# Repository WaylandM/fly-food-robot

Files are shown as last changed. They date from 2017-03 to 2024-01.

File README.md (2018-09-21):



# Cartesian coordinate robot for dispensing fruit fly food

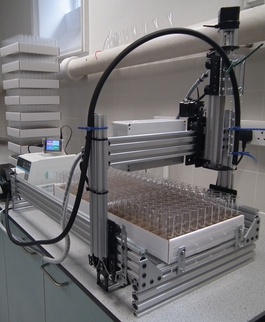
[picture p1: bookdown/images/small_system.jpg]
CNC fly food dispenser


Video: https://doi.org/10.6084/m9.figshare.5175223.v1

## Hardware documentation
The build of the hardware is described on [docubricks](http://docubricks.com/):
[CNC fly food dispenser](http://docubricks.com/viewer.jsp?id=8652757760093769728)

Source of the docubricks documentation:
https://github.com/WaylandM/fly-food-robot/tree/master/docubricks

## Software 
Source code:
https://github.com/WaylandM/fly-food-robot/tree/master/raspberrypi/robot/

## Operating instructions
A bookdown book describing software installation, configuration and operation of the robot can be found here:
https://waylandm.github.io/fly-food-robot/

## Publication
An article providing an overview of this project has been published in the [Journal of Open Hardware](https://openhardware.metajnl.com/):
https://openhardware.metajnl.com/articles/10.5334/joh.9/

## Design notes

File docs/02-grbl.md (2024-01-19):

# Grbl installation and configuration {#grbl}

## Overview

CNC motion control is provided by grbl (https://github.com/gnea/grbl), an open source, embedded, high performance g-code parser. Grbl is written in optimized C and runs directly on an Arduino. This is used in conjunction with the gShield (formerly known as grblshield) which provides the hardware drivers for the stepper motors. Grbl sends out TTL signals on pins A3 and 13 of the Arduino to control coolant flow and spindle direction, respectively. Here these signals are used to remotely control a peristaltic pump. 

## Flashing Grbl to Arduino

To flash Grbl to the Arduino you will need a computer with the latest version of the [Arduino IDE](https://www.arduino.cc/en/Main/Software) installed. The following instructions for flashing Grbl to the Arduino are taken from: https://github.com/gnea/grbl/wiki/Compiling-Grbl

_**NOTE: Before starting, delete prior Grbl library installations from the Arduino IDE. Otherwise, you'll have compiling issues! On a Mac, Arduino libraries are located in ```~/Documents/Arduino/libraries/```. On Windows, it's in ```My Documents\Arduino\libraries```.**_

1. Download the Grbl source code.
 * Open the following page in your web browser: https://github.com/gnea/grbl
 * Click on the ```<>Code``` Tab
 * Click the ```Clone or Download``` green button on the Grbl home page.
 * Click the ```Download ZIP```
 * Unzip the download and you'll have a folder called ```grbl-XXX```, where `XXX` is the release version. 

2. Launch the Arduino IDE (figure \@ref(fig:arduinoIDE))
 * Make sure you are using the most recent version of the Arduino IDE!

<div class="figure" style="text-align: center">
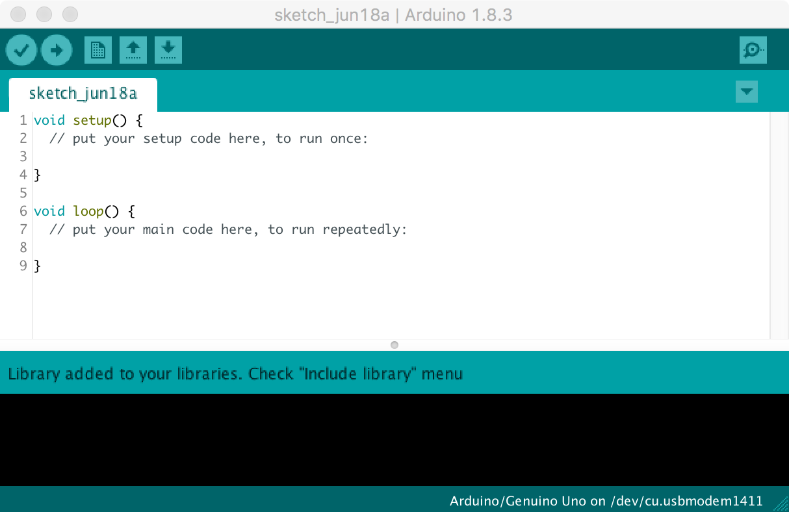
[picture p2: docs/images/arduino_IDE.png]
Arduino IDE

<p class="caption">(\#fig:arduinoIDE)Arduino IDE</p>
</div>

3. Load Grbl into the Arduino IDE as a Library.
 * Click the ```Sketch``` drop-down menu, navigate to ```Include Library``` and select ```Add .ZIP Library```.
 * **IMPORTANT:** Select the ```Grbl``` folder **_inside_** the ```grbl-XXX``` folder, which **only** contains the source files and an example directory (figure \@ref(fig:addGrblLib)).
 
<div class="figure" style="text-align: center">
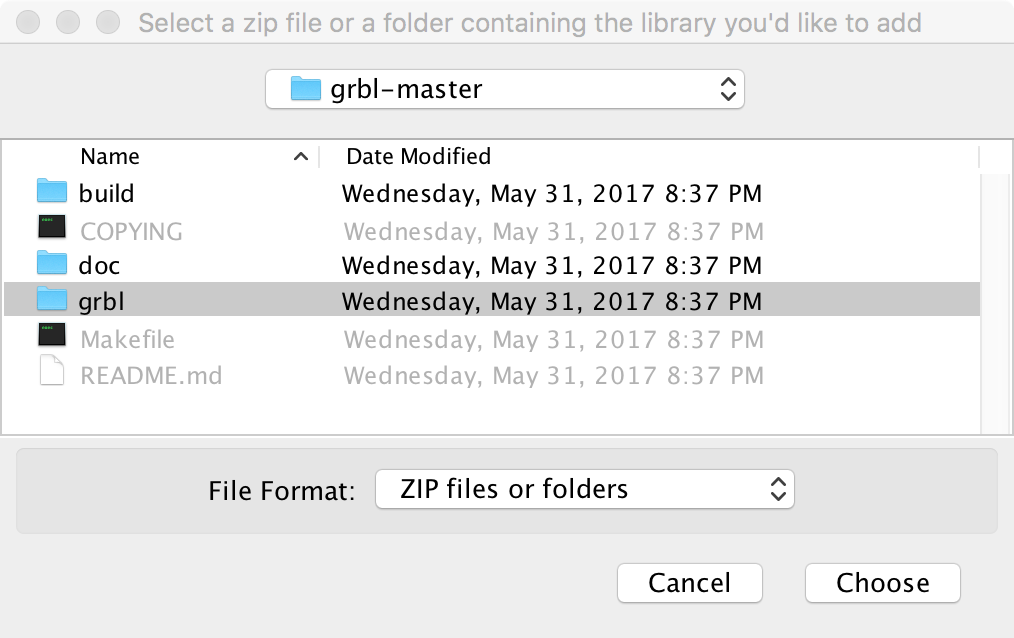
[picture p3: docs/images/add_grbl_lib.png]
Loading Grbl library into the Arduino IDE

<p class="caption">(\#fig:addGrblLib)Loading Grbl library into the Arduino IDE</p>
</div>

 * If you accidentally select the `.zip` file or the wrong folder, you will need to navigate to your Arduino library, delete the mistake, and re-do Step 3.
 
4. Open the `GrblUpload` Arduino example.
 * Click the ```File``` drop-down menu, navigate to ```Examples->Grbl```, and select ```GrblUpload``` (figure \@ref(fig:grblUploadFile)).

<div class="figure" style="text-align: center">
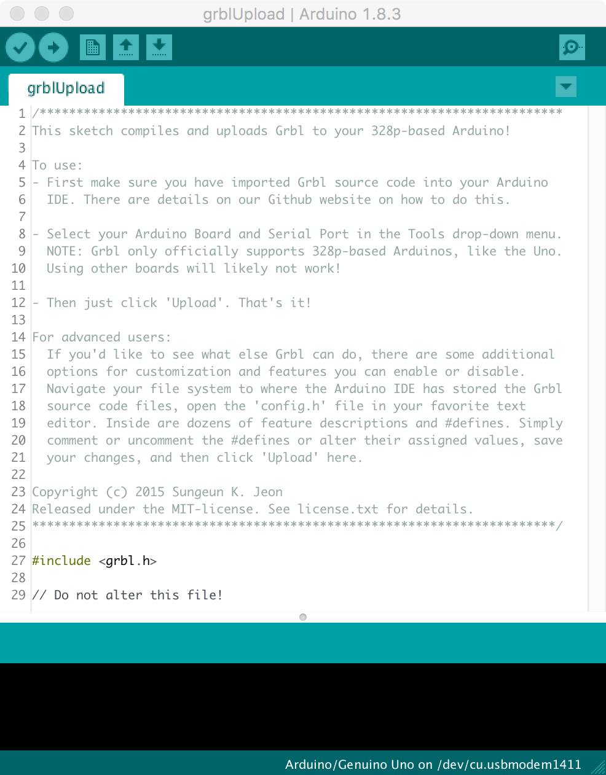
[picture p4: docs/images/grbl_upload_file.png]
GrblUpload example file

<p class="caption">(\#fig:grblUploadFile)GrblUpload example file</p>
</div>

5. Compile and upload Grbl to your Arduino.
 * Connect your computer directly to the Arduino using the USB cable. Unplug the USB cable from the raspberry pi and plug it into your computer. Remember to reconnect the raspberry pi to the Arduino after you have finished configuring Grbl (figure \@ref(fig:laptop2arduino)).

<div class="figure" style="text-align: center">
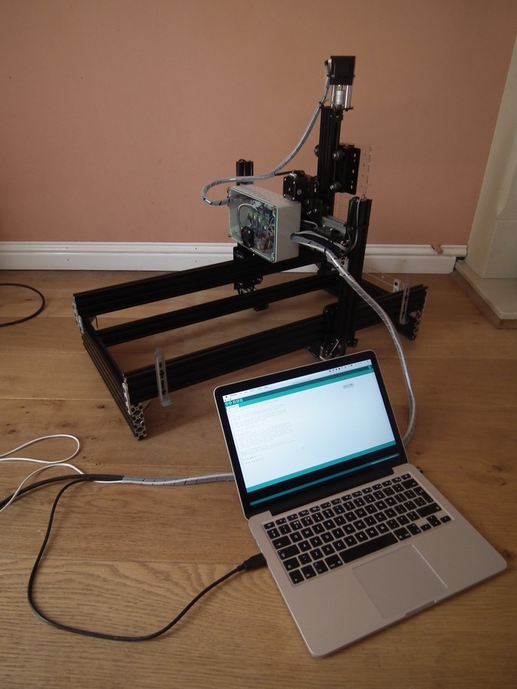
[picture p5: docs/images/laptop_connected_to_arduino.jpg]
Laptop connected directly to Arduino

<p class="caption">(\#fig:laptop2arduino)Laptop connected directly to Arduino</p>
</div>

 * Make sure your board is set to the Arduino Uno in the ```Tool->Board``` menu and the serial port is selected correctly in ```Tool->Serial Port```. 
 * Click the ```Upload```, and Grbl should compile and flash to your Arduino! (Flashing with a programmer also works by using the ```Upload Using Programmer``` menu command.)

## Check serial connection to Grbl

_**NOTE: Before powering up the gShield and motors, check that the actuator carriages for all three axes are approximately centred (figure \@ref(fig:actuatorsCentred)). Initially we do not know in which direction the actuator carriages will travel when G-code commands are issued, so positioning each in the middle of its range reduces the risk of collisions with the end stops.**_

<div class="figure" style="text-align: center">
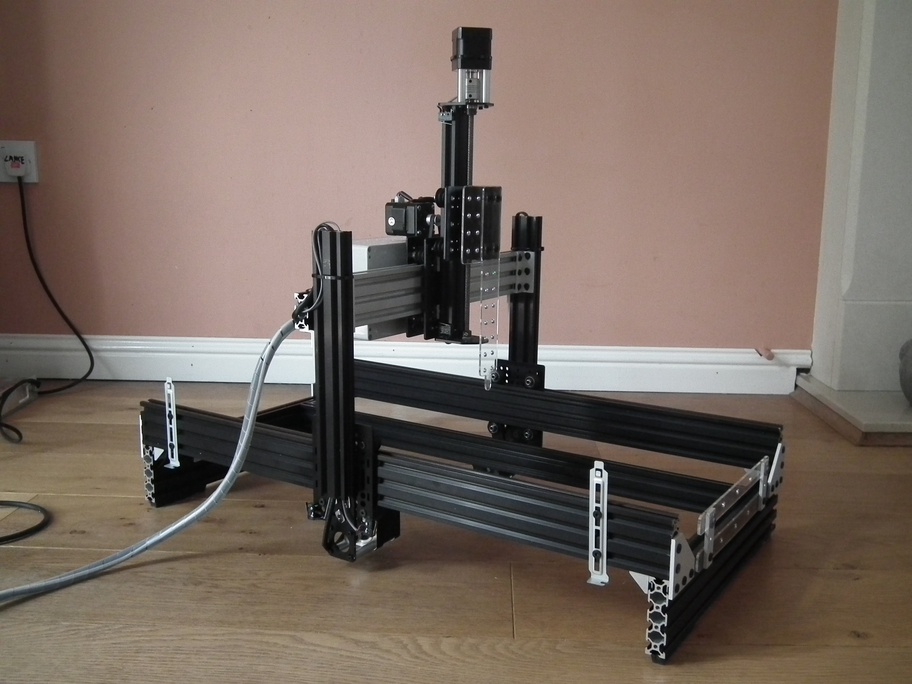
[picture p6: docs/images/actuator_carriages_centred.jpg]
Actuator carriages centred in preparation for powering-up motors for first time

<p class="caption">(\#fig:actuatorsCentred)Actuator carriages centred in preparation for powering-up motors for first time</p>
</div>

1. Open serial monitor in Arduino IDE
 * Click ```Tools``` drop-down menu, and select ```Serial Monitor```

<div class="figure" style="text-align: center">
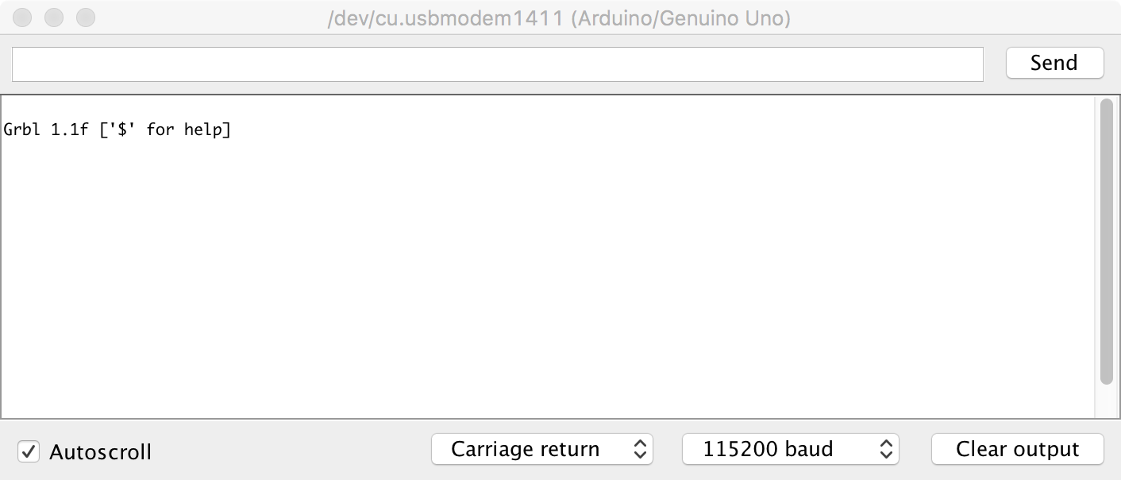
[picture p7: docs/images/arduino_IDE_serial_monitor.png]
Arduino IDE Serial Monitor

<p class="caption">(\#fig:serialMonitor)Arduino IDE Serial Monitor</p>
</div>

 * Note that line-ending is set to ```Carriage return``` and baud rate is set to ```115200``` (figure \@ref(fig:serialMonitor))
2. Try issuing a G-code command. 
 * Type ```?``` and hit return. 
 * This command will report the current position; as we have just started the system up all axes will be at 0.000.
3. Now try moving actuators
 * To move in the x-axis type ```x5``` and hit return. Make a note of the direction in which the actuator carriage moves. N.B. this command tells Grbl to move to the x coordinate that is 5 units from the origin, it is not equivalent to telling the robot to move 5 units in the x-axis.
 * To move in the opposite direction along the x-axis type ```x-5``` and hit return.
 * To return to the starting point, use ```x0```
 * Repeat for the other axes, replacing the x in the commands with y or z. Make a note of the direction the actuator carriages move with each command.

## Grbl configuration

### Read current configuration
 * The ```$$``` command will report Grbl's current configuration.
 * Descriptions of these settings can be found here: https://github.com/gnea/grbl/wiki/Grbl-v1.1-Configuration
 * These settings will be modified in subsequent steps.

### Check directionality of each axis.

<div class="figure" style="text-align: center">
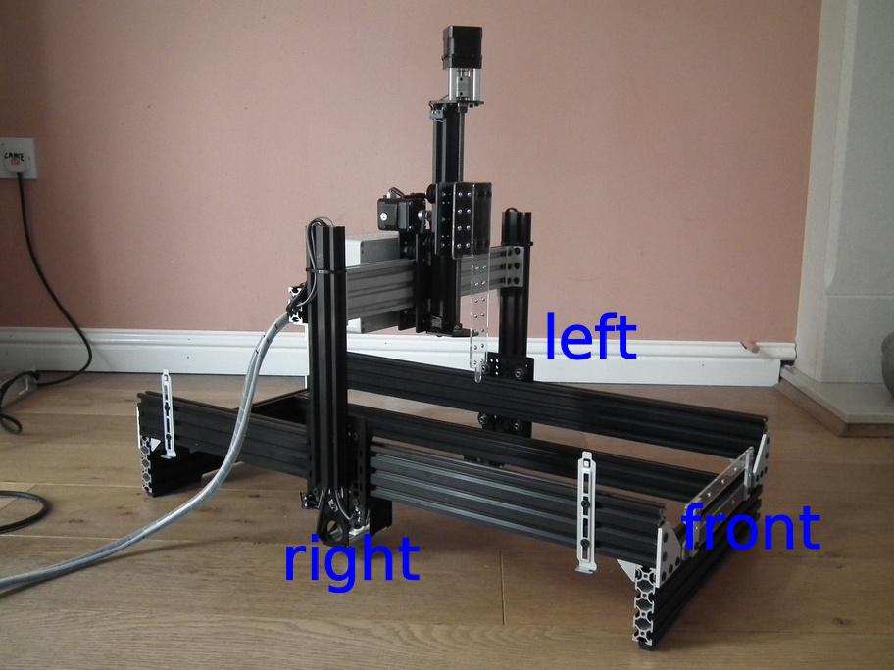
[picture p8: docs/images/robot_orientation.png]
Orientation of robot.

<p class="caption">(\#fig:robotOrientation)Orientation of robot.</p>
</div>

 * Orientation of the robot is shown in figure \@ref(fig:robotOrientation).
 * At present the origins of all three axes are mid-way along each actuator, because this was the position of the actuator carriages when the system was started.
 * Make sure actuator carriages are at their current origin by entering this command: ```x0y0z0```
 * Enter the command: ```x5```. The x-axis carriage should move from right to left (orientation of robot is shown in figure \@ref(fig:robotOrientation). If it doesn't, make a note that it will need to be inverted.
 * Enter the command: ```y5```. The y-axis carriage should move forwards. If it doesn't, make a note that it will need to be inverted.
 * Enter the command: ```z5```. The z-axis carriage should move up. If it doesn't, make a note that it will need to be inverted.
 * The direction of the actuators can be inverted using setting **$3**, the [Direction port invert (mask)](https://github.com/gnea/grbl/wiki/Grbl-v1.1-Configuration#3--direction-port-invert-mask). An appropriate value is selected from table \@ref(tab:invertMaskSettings). For example, to invert the direction of the X and Z axis actuators use the following command: ```$3=5```

<!---
Table: (\#tab:invertMaskSettings) Masks for direction port inversion.

| Setting Value | Mask |Invert X | Invert Y | Invert Z |
|:-------------:|:----:|:-------:|:--------:|:--------:|
| 0 | 00000000 |N | N | N |
| 1 | 00000001 |Y | N | N |
| 2 | 00000010 |N | Y | N |
| 3 | 00000011 |Y | Y | N |
| 4 | 00000100 |N | N | Y |
| 5 | 00000101 |Y | N | Y |
| 6 | 00000110 |N | Y | Y |
| 7 | 00000111 |Y | Y | Y |

 --->

Table: (\#tab:invertMaskSettings)Masks for direction port inversion.

|Setting Value |Mask     |Invert X |Invert Y |Invert Z |
|:-------------|:--------|:--------|:--------|:--------|
|0             |00000000 |N        |N        |N        |
|1             |00000001 |Y        |N        |N        |
|2             |00000010 |N        |Y        |N        |
|3             |00000011 |Y        |Y        |N        |
|4             |00000100 |N        |N        |Y        |
|5             |00000101 |Y        |N        |Y        |
|6             |00000110 |N        |Y        |Y        |
|7             |00000111 |Y        |Y        |Y        |

### Activate hard limits
Hard limits are a safety feature to prevent the machine from travelling beyond the limits of travel. Grbl monitors the paired limit switches on each axis and if a switch is triggered it will immediately switch off all motors. Hard limits are activated by setting **$21** [hard limits ( boolean)](https://github.com/gnea/grbl/wiki/Grbl-v1.1-Configuration#21---hard-limits-boolean) to 1: 
```
$21=1
```

### Setup homing
The homing cycle is used to set the origin of the Cartesian coordinate system used by the robot. During the homing cycle Grbl moves each actuator in the positive direction until the limit switches are triggered. The homing cycle is activated by setting **$22** [homing cycle (boolean)](https://github.com/gnea/grbl/wiki/Grbl-v1.1-Configuration#22---homing-cycle-boolean) to 1: 
```
$22=1
```

Initiate  a homing cycle using the following command: ```$h```. All actuator carriages should move to the origin of their axes. The origin of the Cartesian coordinate system (home) for the robot is shown in figures \@ref(fig:xyOrigin) and \@ref(fig:zOrigin)

<div class="figure" style="text-align: center">
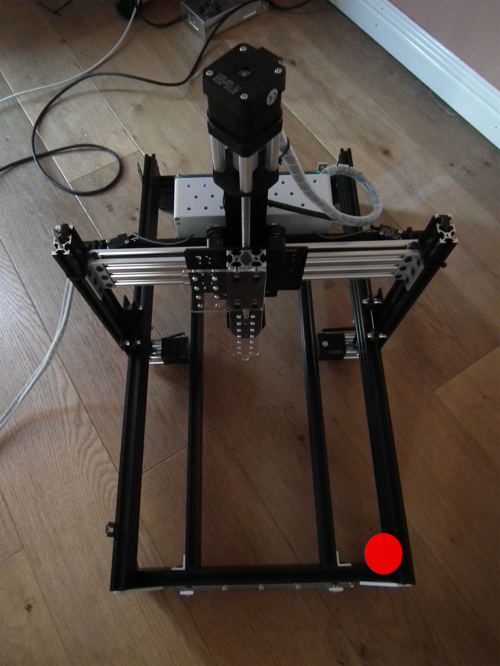
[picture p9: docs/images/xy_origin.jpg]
Origin of XY coordinate system.

<p class="caption">(\#fig:xyOrigin)Origin of XY coordinate system.</p>
</div>

<div class="figure" style="text-align: center">
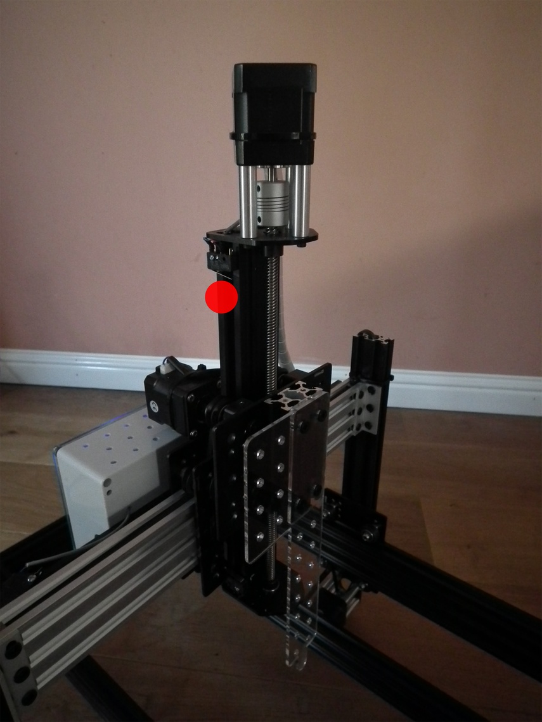
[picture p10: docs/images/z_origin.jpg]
Origin of Z axis.

<p class="caption">(\#fig:zOrigin)Origin of Z axis.</p>
</div>

We also need to set **$24** [homing feed rate](https://github.com/gnea/grbl/wiki/Grbl-v1.1-Configuration#24---homing-feed-mmmin) and **$25** [homing seek rate](https://github.com/gnea/grbl/wiki/Grbl-v1.1-Configuration#25---homing-seek-mmmin). Homing seek rate is the initial speed at which Grbl searches for the limit switches. Once it has them, it makes slower approach at the homing feed rate to get a more precise location for machine zero. We will set homing seek rate to 1000 mm/min ```$24=100``` and homing feed rate to 100 mm/min ```$25=1000```.

At the end of a homing cycle each actuator carriage must be moved off its home limit switch, otherwise the hard limit will be triggered. 
The **$27** [Homing pull-off (mm)](https://github.com/gnea/grbl/wiki/Grbl-v1.1-Configuration#27---homing-pull-off-mm) specifies the distance required to clear the limit switches. For our robot we will use a value of 5mm:
```
$27=5
```

### Motor step size
**$100**, **$101** and **$102** define [[X,Y,Z] steps/mm](https://github.com/gnea/grbl/wiki/Grbl-v1.1-Configuration#100-101-and-102--xyz-stepsmm).
Suitable values for our stepper motors are:
```
$100=40
$101=40
$102=49.673
```

If you are using a different type of stepper motor, the step size can be easily calculated by measuring how far each actuator moves in response to a G-code command. For example, we would calculate the step size for the X actuator as follows.

1. Using the serial monitor in the Arduino IDE, issue the following command to *home* the machine:
```
$h
```

2. Read the current position of the machine, as reported by the Grbl controller:
```
?
```
After homing the Cartesian coordinates should be zero minus the homing pull-off:
* x = -5
* y = -5
* z = -5

3. Make a note of the physical position of the nozzle.

4. Issue a g-code command to move to the -100mm position on the x-axis:
```
x-100
```
Keep decreasing the value of x until the x-actuator carriage almost meets the limit switch on the right hand side of the machine. The greater the distance moved, the more precise our calculation of step-size will be.

5. Query Grbl's machine coordinates:
```
?
```

6. Measure the physical distance travelled along the x-axis in millimetres.

7. Find **$100**, the currently configured step size for the x-axis:
```
$$
```

8. Calculate the correct value for step-size:

```
current_step_size = steps/mm in current configuration
grbl_start = start position reported by Grbl controller (mm)
grbl_end = end position reported by Grbl controller (mm)
physical_distance = physical distance moved by actuator (mm)

steps/mm = -(curr_steps_per_mm * (end_pos_grbl-start_pos_grbl)) / physical_distance
```

### Feed rates and acceleration
**$110**, **$111** and **$112** set the [maximum rates (mm/min)](https://github.com/gnea/grbl/wiki/Grbl-v1.1-Configuration#110-111-and-112--xyz-max-rate-mmmin) for the X, Y and Z actuators, respectively. We will use the following values:
```
$110=5000
$111=5000
$112=2500
```

[Acceleration (mm/sec^2)](https://github.com/gnea/grbl/wiki/Grbl-v1.1-Configuration#120-121-122--xyz-acceleration-mmsec2) is set to 50 for all axes:
```
$120=50
$121=50
$122=50
```

### Summary of settings
```
$0=10
$1=25
$2=0
$3=5
$4=0
$5=0
$6=0
$10=1
$11=0.010
$12=0.002
$13=0
$20=0
$21=1
$22=1
$23=0
$24=100.000
$25=1000.000
$26=250
$27=5.000
$30=1000
$31=0
$32=0
$100=40.000
$101=40.000
$102=49.673
$110=5000.000
$111=5000.000
$112=2500.000
$120=50.000
$121=50.000
$122=50.000
$130=200.000
$131=500.000
$132=200.000
```

## Setting motor current

The gShield has trimpots for adjusting the motor current of each axis, as shown in figure \@ref(fig:gShield).

<div class="figure" style="text-align: center">
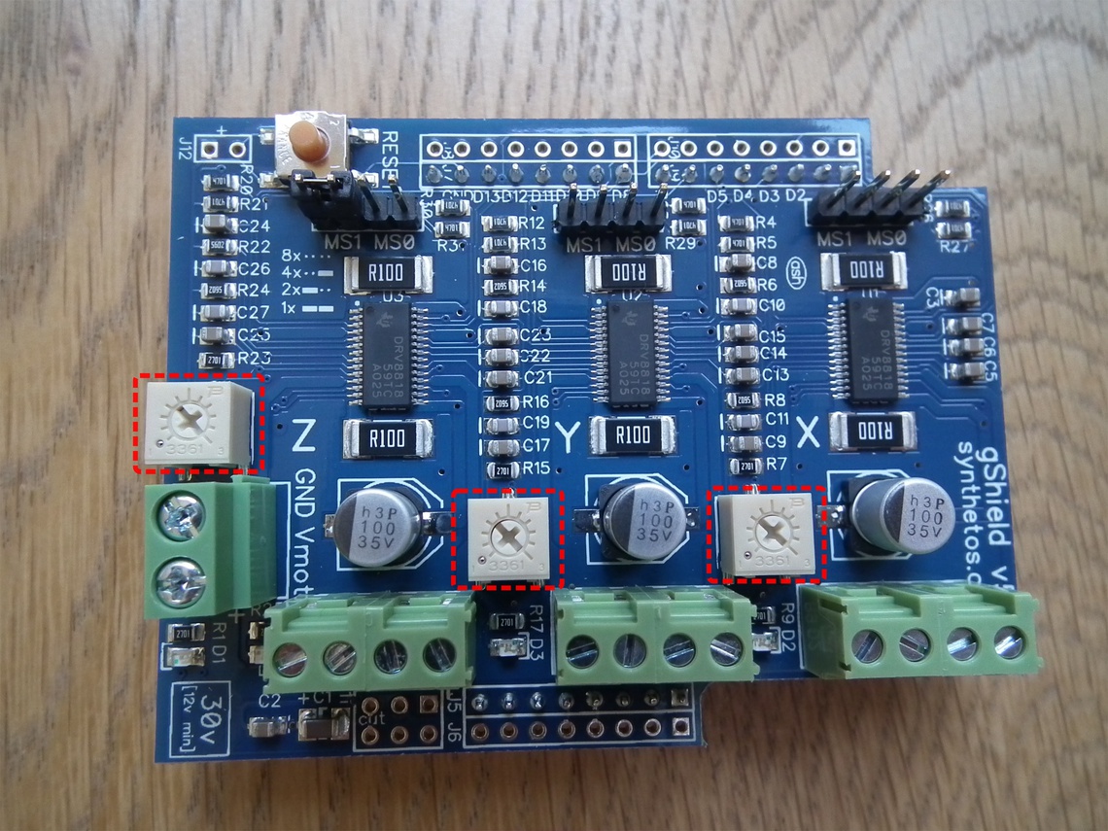
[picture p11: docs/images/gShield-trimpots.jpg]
gShield trimpots

<p class="caption">(\#fig:gShield)gShield trimpots</p>
</div>

Instructions for setting motor current are provided here:
https://github.com/synthetos/grblShield/wiki/Using-grblShield#setting-motor-current

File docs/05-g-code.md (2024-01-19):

# Program robot to fill vials {#gcode}

<!--
# need 8-9 ml
# pump speed 1800ml/min
# ml/s = 1800/60 = 30
# fill time = 0.3
-->

<!--
ssh pi@192.168.1.3

sudo minicom -D /dev/ttyACM0 -b115200

?<Idle|MPos:-5.000,-5.000,-4.993|FS:0,0|Ov:100,100,100>

x-10 y-10 z-10
ok
?<Idle|MPos:-10.000,-10.000,-10.005|FS:0,0>

x-20 y-20 z-30
ok
?<Idle|MPos:-20.000,-20.000,-29.996|FS:0,0>

x-8 y-14 z-62
ok
?<Idle|MPos:-8.000,-14.000,-62.006|FS:0,0>

./robot/py/calibrate_pump.py

./robot/py/stream2.py robot/nc/calibrate_pump.nc /dev/ttyACM0

./robot/py/fill_boxes.py

-->

## Overview
The movement of the robot is programmed in [G-code](https://en.wikipedia.org/wiki/G-code). We only need nine G-code commands to control the robot (table \@ref(tab:gCodes)).

Table: (\#tab:gCodes)G-code commands used to control robot.

|Code |Description                                        |
|:----|:--------------------------------------------------|
|x    |absolute position of x-axis                        |
|y    |absolute position of y-axis                        |
|z    |absolute position of z-axis                        |
|g4   |dwell time (control parameter p specifies seconds) |
|m3   |set pump rotation to clockwise                     |
|m4   |set pump rotation to counter clockwise             |
|m8   |start pump                                         |
|m9   |stop pump                                          |
|$h   |initiate homing cycle                              |

A G-code program for filling vials of food could be created manually, by listing the necessary commands sequentially in a text file.  However, this would be laborious and error prone. If the size of the boxes of vials are known, the G-code can be programmatically generated. 

## Load boxes {#loadBoxes}

<div class="figure" style="text-align: center">
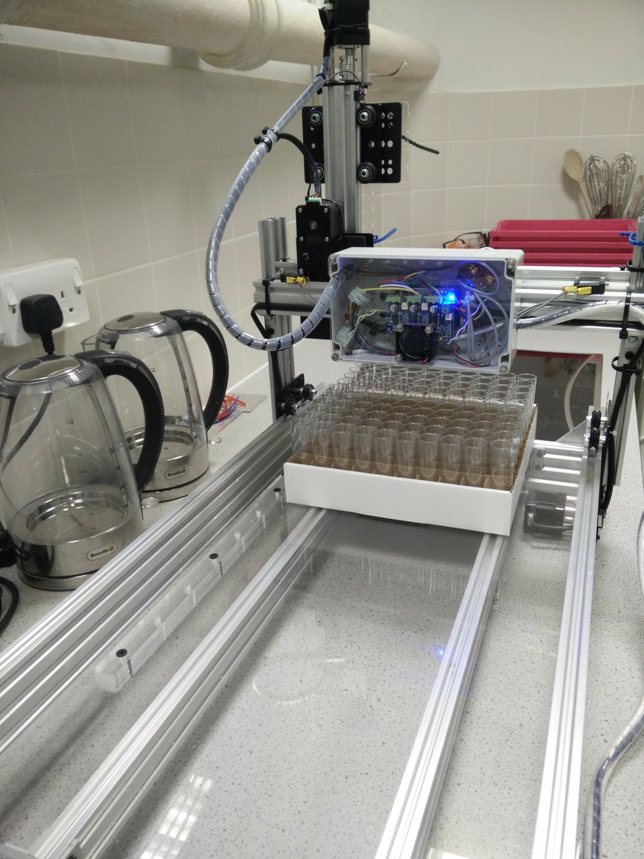
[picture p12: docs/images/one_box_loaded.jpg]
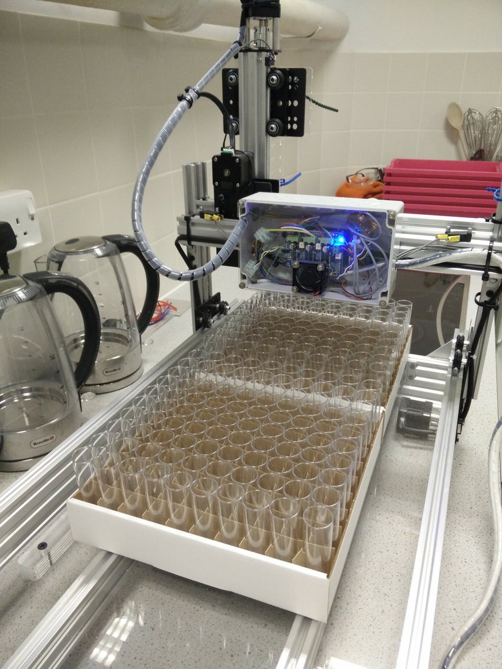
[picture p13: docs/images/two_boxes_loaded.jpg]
Loading boxes of vials.

<p class="caption">(\#fig:loadBoxes2)Loading boxes of vials.</p>
</div>

Load boxes onto the platform of the robot (figure \@ref(fig:loadBoxes2)).
 * The first box should be flush with the fence and the guide rail.
 * The second box should be flush with the first and the guide rail.
 * The boxes we are using have a pair of double-thickness side-walls and a pair of single-thickness side-walls. The pairs are on opposite sides of the box. With this type of box it is important to note the orientation of the boxes when the Cartesian coordinates of the vials are determined, because the same orientation must be used when filling vials with food. We load the boxes with a double-thickness side-wall facing forwards.

## Determine box coordinates {#boxCoordinates}

We need to determine the Cartesian coordinates of vials in diagonally opposite corners of each box.

1. Login to raspberry pi using ssh. My raspberry pi has the IP address 192.168.1.3 and so I would use:
* ``` ssh pi@192.168.1.3 ```
* Default password for the **pi** user account is 'raspberry'.

2. Use minicom to connect to the Grbl controller running on the Arduino, so that we can interactively control the robot from the command line:
```
sudo minicom -D /dev/ttyACM0 -b115200
```

3. Make sure nozzle is at ** home ** position by issuing homing command:
```
$h
```

4. First we will determine the Cartesian coordinates of the vial in the front left corner of the first box.

* Make small movements in X and Y until the nozzle is centred over this vial, *e.g.*:
```
x-8 y-8
```

* Lower the nozzle in small increments until it is just 2-3mm above the the top of the vial (figure \@ref(fig:box1FrontLeft)), *e.g.*:
```
z-20
```

* Query the current X, Y and Z coordinates by issuing the following command:
```
?
```
Make a note of all three coordinates. 

<div class="figure" style="text-align: center">
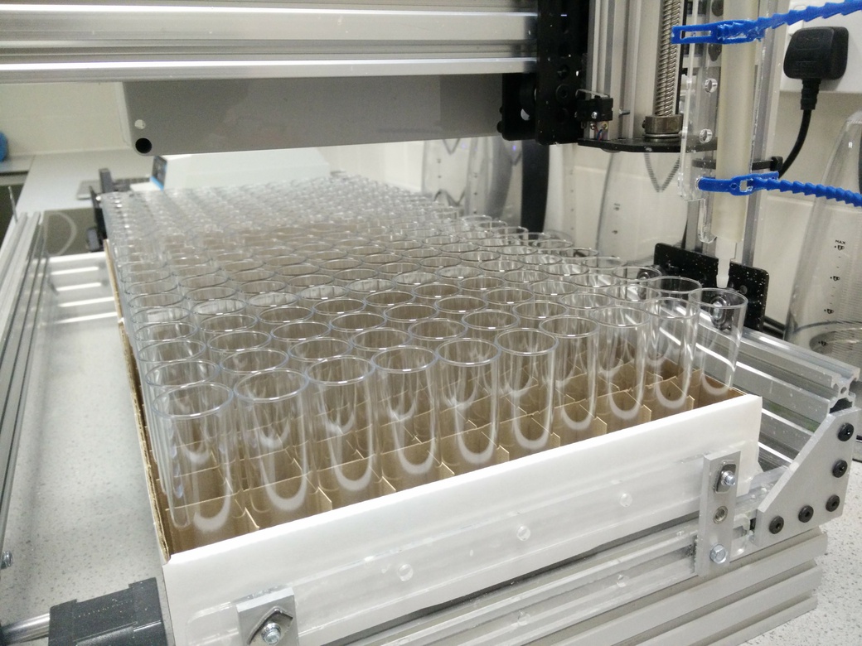
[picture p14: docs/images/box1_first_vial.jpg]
Nozzle positioned over the front left vial in box 1.

<p class="caption">(\#fig:box1FrontLeft)Nozzle positioned over the front left vial in box 1.</p>
</div>

5. Issue G-code commands to move the nozzle laterally until it is over the back right vial of the first box (figure \@ref(fig:box1BackRight)).

<div class="figure" style="text-align: center">
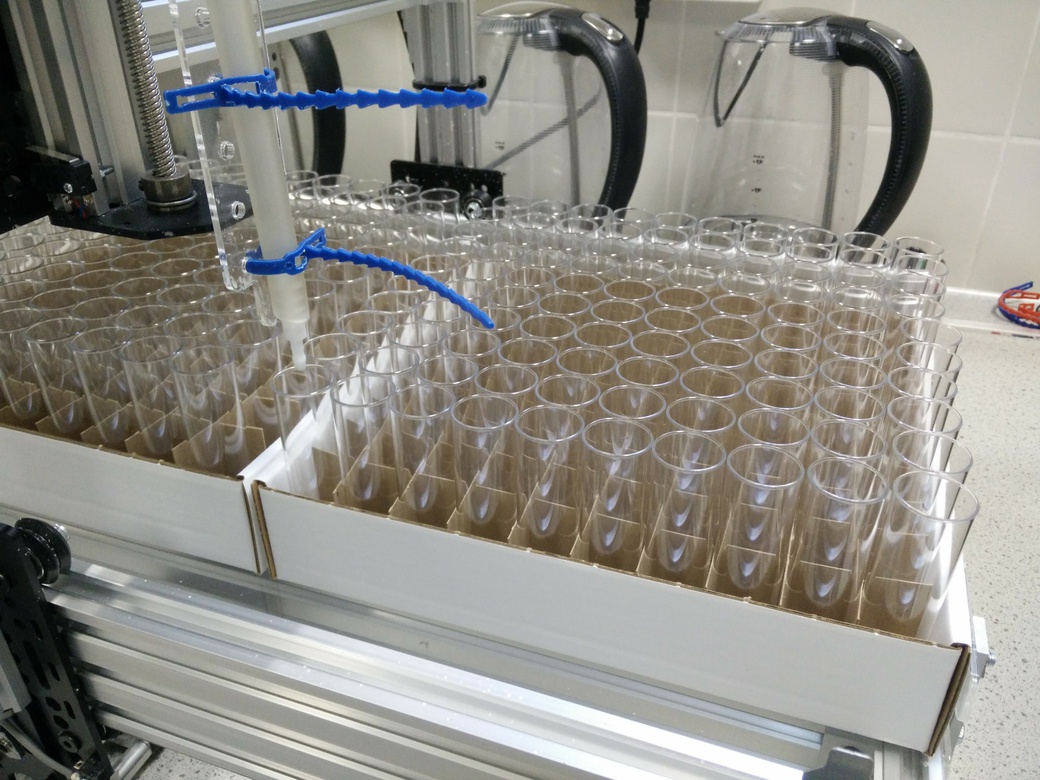
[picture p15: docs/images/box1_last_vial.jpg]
Nozzle positioned over the back right vial in box 1.

<p class="caption">(\#fig:box1BackRight)Nozzle positioned over the back right vial in box 1.</p>
</div>
* Use ```?``` command to query nozzle position, and make a note of the X and Y coordinates:

6. Move the nozzle laterally until it is over the front left vial of the second box (figure \@ref(fig:box2FrontLeft)), then record X and Y coordinates.

<div class="figure" style="text-align: center">
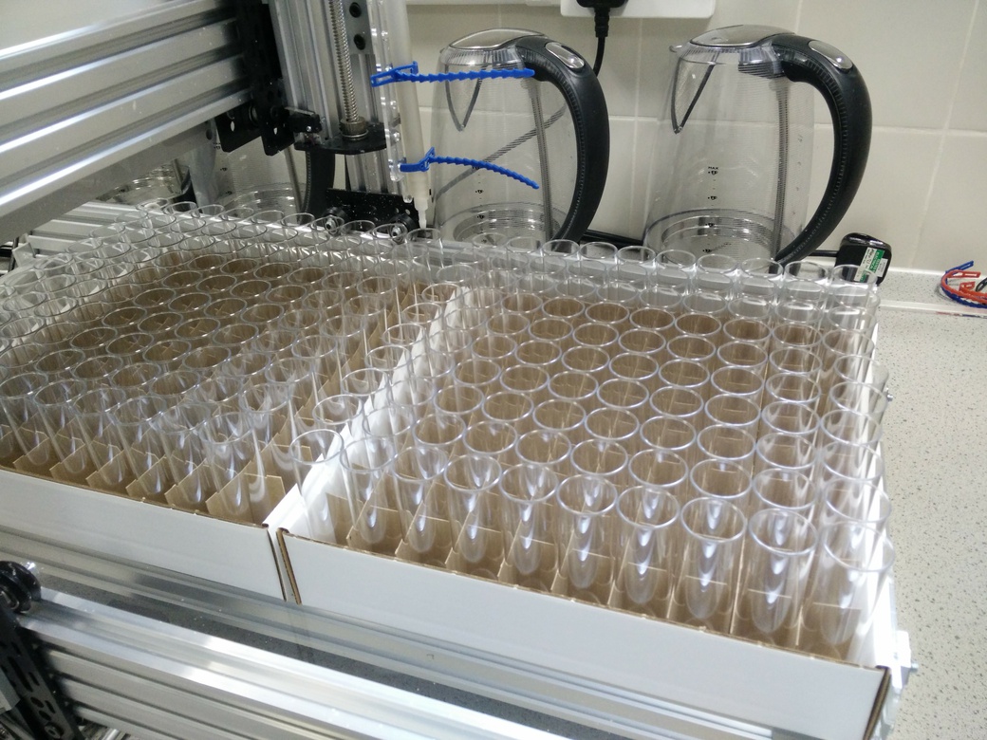
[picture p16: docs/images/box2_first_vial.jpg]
Nozzle positioned over the front left vial in box 2.

<p class="caption">(\#fig:box2FrontLeft)Nozzle positioned over the front left vial in box 2.</p>
</div>

7. Finally determine the X and Y coordinates of the back right vial in the second box (figure \@ref(fig:box2BackRight)).

<div class="figure" style="text-align: center">
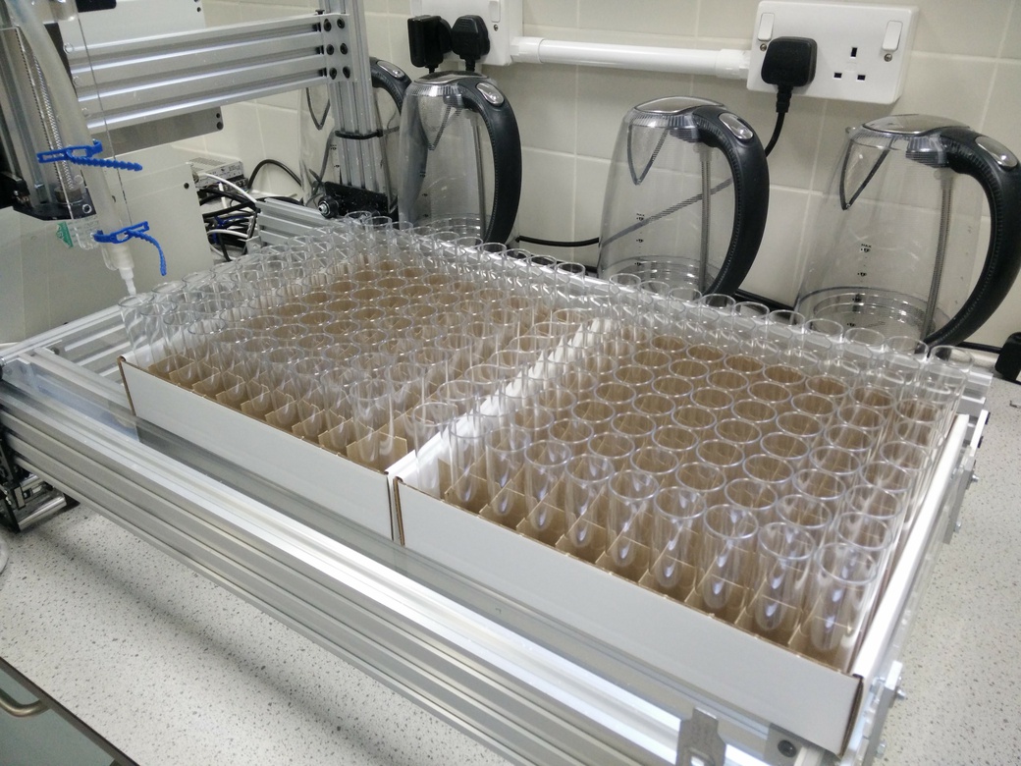
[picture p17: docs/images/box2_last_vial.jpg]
Nozzle positioned over the back right vial in box 2.

<p class="caption">(\#fig:box2BackRight)Nozzle positioned over the back right vial in box 2.</p>
</div>

## Calibrate pump {#calibratePump}
<!--
# need 8-9 ml
# pump speed 1800ml/min
# ml/s = 1800/60 = 30
# fill time = 0.3
-->
The peristaltic pump is started and stopped using the ```m8``` and ```m9``` G-code commands, respectively (table \@ref(tab:gCodes)). To maximize speed, the pump will be run at its maximum flow rate of 30ml/second. In our fly facility, we add 9ml of food to each vial, therefore based on the maximum flow rate, we should only need to run the pump for 0.3 seconds to dispense 9ml of food. However, there is latency in the system and the pump does not reach its maximum flow rate instantaneously on activation. Therefore, it is important to determine the *fill time* empirically. We do this by programming the robot to test fill a single box of vials using a range of *fill times*. The **calibrate_pump.py** script downloaded to the Raspberry Pi in stage \@ref(installScripts) can be used to generate the appropriate G-code program. 

1. Open **calibrate_pump.py** for editing:
```
sudo nano /home/pi/robot/py/calibrate_pump.py
```

2. Near the top of the file (line 32 onwards) are various settings to be modified:

``` 

# SETTINGS

# filename
filename = '/home/pi/robot/nc/calibrate_pump.nc'

# home/datum + homing pull-off (mm) (value of Grbl setting $27)
x_home = -5
y_home = -5
z_home = -5

# z value providing minimal clearance between nozzle and top of vials
z_fill = -62 

# peristaltic pump settings
min_fill_time = 0.3
max_fill_time = 0.6
# pause to allow for drips before moving to next vial
drip_pause = 0.1 

# vial coordinates (x,y)
frontLeft = (-8,-14)
backRight = (-236,-240)

nrows=10
ncols=10
```

* The **filename** is the full path to the G-code file that will be generated by the python script. 
* The parameters **x_home, y_home** and **z_home** are the Cartesian coordinates of the home position (*i.e.* home/datum + homing pull-off (mm)). 
* Modify **z_fill** to the appropriate nozzle height for filling vials (this was determined in step 5 of section \@ref(boxCoordinates)). 
* The **min_fill_time** should be set to our estimate of *fill time* based on the pump's specified flow rate. We will set **max_fill_time** to twice the value of **min_fill_time**.
* The vial coordinates (**frontLeft** and **frontRight**) are those determined for the front left and back right vials in the first box (refer to steps 5 and 6 of section \@ref(boxCoordinates)). 
* Our boxes have ten rows, each containing ten vials, so we set **nrows** and **ncols** to 10.

3. After editing the settings in **calibrate_pump.py**, run the script to generate a G-code program:
```
./robot/py/calibrate_pump.py
```
This will generate a G-code program: **/home/pi/robot/nc/calibrate_pump.nc** which will iteratively increase the fill time for each successive row of vials. The **min_fill_time** will be used for the first row of vials and the fill time will be increased by (**max_fill_time** - **min_fill_time**) / (**nrows** - 1.0) for each successive row (*e.g.* table \@ref(tab:calibrationFillTimes)). Note that the fill times are rounded to the nearest 100th of a second. The fill time for each row is listed in the comments at the top of the **/home/pi/robot/nc/calibrate_pump.nc** file; to view this information run:
```
head -n12 ~/robot/nc/calibrate_pump.nc
```

Table: (\#tab:calibrationFillTimes)Example calibration fill times.

| Box Row| Fill Time|
|-------:|---------:|
|       1|      0.30|
|       2|      0.33|
|       3|      0.37|
|       4|      0.40|
|       5|      0.43|
|       6|      0.47|
|       7|      0.50|
|       8|      0.53|
|       9|      0.57|
|      10|      0.60|

4. Send the G-code pump-calibration program to the Grbl controller
**/home/pi/robot/py/stream2.py** can be used to stream a text file of G-code commands to Grbl: 
```
./robot/py/stream2.py robot/nc/calibrate_pump.nc /dev/ttyACM0
```
Once the robot has completed the calibration run and returned the nozzle to the home position, inspect the fill level in each row of vials. Identify the row in which vials are filled with the desired volume of food and then refer to the **/home/pi/robot/calibrate_pump.nc** file to find out the fill time used for that particular row.

## Generate programs
Once the pump has been calibrated we are ready to generate the G-code instructions for the routine filling of vials. The **fill_boxes.py** script downloaded to the Raspberry Pi in stage \@ref(installScripts) is used to generate two G-code programs: 

* **1_box.nc** - fill one box of vials
* **2_boxes.nc** - fill two boxes of vials

1. Open **fill_boxes.py** for editing:
```
sudo nano /home/pi/robot/py/fill_boxes.py
```

2. Near the top of the file (line 32 onwards) are various settings to be modified:

```

# SETTINGS
# modify values of variables in this section to match your system

# filenames
filename1Box = '/home/pi/robot/nc/1_box.nc'
filename2Boxes = '/home/pi/robot/nc/2_boxes.nc'

# home/datum + homing pull-off (mm) (value of Grbl setting $27)
x_home = -5
y_home = -5
z_home = -5

# z value providing minimal clearance between nozzle and top of vials
z_fill = -62 

# peristaltic pump settings
fill_time = 0.43
# pause to allow for drips before moving to next vial
drip_pause = 0.1 

# vial coordinates (x,y)
box1FrontLeft = (-8,-14)
box1BackRight = (-236,-240)
box2FrontLeft = (-8,-286)
box2BackRight = (-236,-513)

nrows=10
ncols=10
nVials=nrows*ncols
```

* **filename1Box** and **filename2Boxes** specify the filename and full path to the two G-code programs that will be generated. You should not need to modify these values. The GUI script (**/home/pi/robot/py/fly_gui.py**) expects the two programs to have the default names and paths; if you alter the names or paths of these files, you will need to edit the GUI script.
* The parameters **x_home, y_home** and **z_home** are the Cartesian coordinates of the home position (*i.e.* home/datum + homing pull-off (mm)). 
* Modify **z_fill** to the appropriate nozzle height for filling vials (this was determined in step 5 of section \@ref(boxCoordinates)). 
* **fill_time** was determined in the previous section \@ref(calibratePump).
* The default value of **drip_pause** should be appropriate for most systems.
* The vial coordinates (**box1FrontLeft**, **box1BackRight**, **box2FrontLeft** and **box2BackRight**) were determined in section \@ref(boxCoordinates).
* Our boxes have ten rows, each containing ten vials, so we set **nrows** and **ncols** to 10.

3. After editing the settings in **fill_boxes.py**, run the script to generate the two G-code programs:
```
./robot/py/fill_boxes.py
```

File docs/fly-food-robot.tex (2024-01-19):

% Options for packages loaded elsewhere
\PassOptionsToPackage{unicode}{hyperref}
\PassOptionsToPackage{hyphens}{url}
%
\documentclass[
]{book}
\usepackage{amsmath,amssymb}
\usepackage{iftex}
\ifPDFTeX
  \usepackage[T1]{fontenc}
  \usepackage[utf8]{inputenc}
  \usepackage{textcomp} % provide euro and other symbols
\else % if luatex or xetex
  \usepackage{unicode-math} % this also loads fontspec
  \defaultfontfeatures{Scale=MatchLowercase}
  \defaultfontfeatures[\rmfamily]{Ligatures=TeX,Scale=1}
\fi
\usepackage{lmodern}
\ifPDFTeX\else
  % xetex/luatex font selection
\fi
% Use upquote if available, for straight quotes in verbatim environments
\IfFileExists{upquote.sty}{\usepackage{upquote}}{}
\IfFileExists{microtype.sty}{% use microtype if available
  \usepackage[]{microtype}
  \UseMicrotypeSet[protrusion]{basicmath} % disable protrusion for tt fonts
}{}
\makeatletter
\@ifundefined{KOMAClassName}{% if non-KOMA class
  \IfFileExists{parskip.sty}{%
    \usepackage{parskip}
  }{% else
    \setlength{\parindent}{0pt}
    \setlength{\parskip}{6pt plus 2pt minus 1pt}}
}{% if KOMA class
  \KOMAoptions{parskip=half}}
\makeatother
\usepackage{xcolor}
\usepackage{longtable,booktabs,array}
\usepackage{calc} % for calculating minipage widths
% Correct order of tables after \paragraph or \subparagraph
\usepackage{etoolbox}
\makeatletter
\patchcmd\longtable{\par}{\if@noskipsec\mbox{}\fi\par}{}{}
\makeatother
% Allow footnotes in longtable head/foot
\IfFileExists{footnotehyper.sty}{\usepackage{footnotehyper}}{\usepackage{footnote}}
\makesavenoteenv{longtable}
\usepackage{graphicx}
\makeatletter
\def\maxwidth{\ifdim\Gin@nat@width>\linewidth\linewidth\else\Gin@nat@width\fi}
\def\maxheight{\ifdim\Gin@nat@height>\textheight\textheight\else\Gin@nat@height\fi}
\makeatother
% Scale images if necessary, so that they will not overflow the page
% margins by default, and it is still possible to overwrite the defaults
% using explicit options in \includegraphics[width, height, ...]{}
\setkeys{Gin}{width=\maxwidth,height=\maxheight,keepaspectratio}
% Set default figure placement to htbp
\makeatletter
\def\fps@figure{htbp}
\makeatother
\usepackage{soul}
\setlength{\emergencystretch}{3em} % prevent overfull lines
\providecommand{\tightlist}{%
  \setlength{\itemsep}{0pt}\setlength{\parskip}{0pt}}
\setcounter{secnumdepth}{5}
\usepackage{booktabs}
\usepackage{amsthm}
\makeatletter
\def\thm@space@setup{%
  \thm@preskip=8pt plus 2pt minus 4pt
  \thm@postskip=\thm@preskip
}
\makeatother
\ifLuaTeX
  \usepackage{selnolig}  % disable illegal ligatures
\fi
\usepackage[]{natbib}
\bibliographystyle{apalike}
\IfFileExists{bookmark.sty}{\usepackage{bookmark}}{\usepackage{hyperref}}
\IfFileExists{xurl.sty}{\usepackage{xurl}}{} % add URL line breaks if available
\urlstyle{same}
\hypersetup{
  pdftitle={CNC Fly Food Dispenser},
  pdfauthor={Matt Wayland},
  hidelinks,
  pdfcreator={LaTeX via pandoc}}

\title{CNC Fly Food Dispenser}
\author{Matt Wayland}
\date{2024-01-19}

\begin{document}
\maketitle

{
\setcounter{tocdepth}{1}
\tableofcontents
}
\hypertarget{preface}{%
\chapter*{Preface}\label{preface}}
\addcontentsline{toc}{chapter}{Preface}

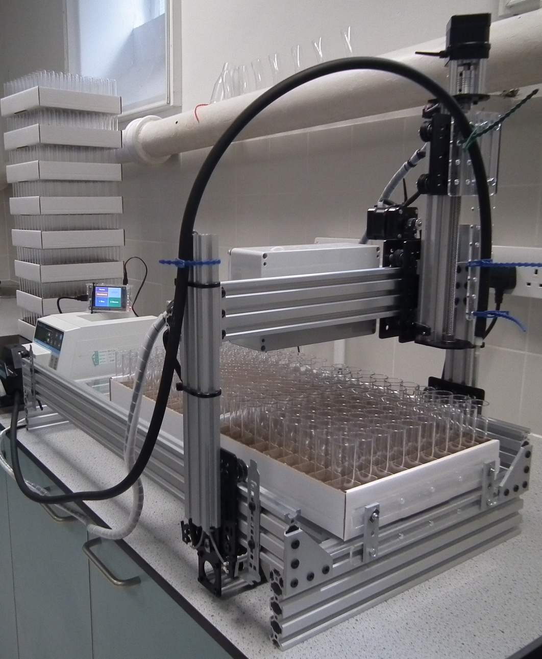
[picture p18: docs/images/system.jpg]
\begin{center} \end{center}

\hypertarget{github}{%
\section*{Github}\label{github}}
\addcontentsline{toc}{section}{Github}

\href{https://github.com/WaylandM/fly-food-robot}{WaylandM/fly-food-robot}

\hypertarget{license}{%
\section*{License}\label{license}}
\addcontentsline{toc}{section}{License}

License for software and documentation:
\href{https://www.gnu.org/licenses/gpl-3.0.en.html}{GPL-3}

\hypertarget{contact}{%
\section*{Contact}\label{contact}}
\addcontentsline{toc}{section}{Contact}

Matt Wayland

\hypertarget{publication}{%
\section*{Publication}\label{publication}}
\addcontentsline{toc}{section}{Publication}

Article in \href{https://openhardware.metajnl.com/}{Journal of Open Hardware}:
\url{https://openhardware.metajnl.com/articles/10.5334/joh.9/}

\hypertarget{colophon}{%
\section*{Colophon}\label{colophon}}
\addcontentsline{toc}{section}{Colophon}

This book was produced using the \textbf{bookdown} package \citep{R-bookdown}, which was built on top of R Markdown and \textbf{knitr} \citep{xie2015}.

\hypertarget{intro}{%
\chapter{Introduction}\label{intro}}

The fruit fly, \emph{Drosophila melanogaster}, is one of the most important model organisms in biological research. Maintaining stocks of fruit flies in the laboratory is labour-intensive. One task which lends itself to automation is the production of the vials of food in which the flies are reared. Fly facilities typically have to generate several thousand vials of fly food each week to sustain their fly stocks. The system presented here combines a Cartesian coordinate robot with a peristaltic pump (Figure \ref{fig:architecture}). The design of the robot is based on the Routy CNC Router created by Mark Carew (\url{http://openbuilds.org/builds/routy-cnc-router-v-slot-belt-pinion.101/}), and uses belt and pully actuators for the X and Y axes, and a leadscrew actuator for the Z axis. CNC motion and operation of the peristaltic pump are controlled by grbl (\url{https://github.com/gnea/grbl}), an open source, embedded, high performance g-code parser. Grbl is written in optimized C and runs directly on an Arduino. A Raspberry Pi is used to generate and stream G-code instructions to Grbl. A touch screen on the Raspberry Pi provides a graphical user interface to the system. The system has capacity to fill two boxes of fly food vials at a time. Instructions for building the hardware are available on \href{http://docubricks.com/viewer.jsp?id=8652757760093769728}{DocuBricks}.

\begin{figure}

{\centering  

}

\caption{System architecture.}\label{fig:architecture}
\end{figure}

Software installation and configuration on the Arduino and raspberry pi are detailed in chapters \ref{grbl} and \ref{raspi}. Chapter \ref{gcode} explains how to program the robot to fill vials of fly food. Instructions for the routine use of the robot are provided in chapter \ref{operation}. To see a video of the robot in action, go to:

\url{https://doi.org/10.6084/m9.figshare.5175223.v1}

An article providing an overview of this project has been published in the \href{https://openhardware.metajnl.com/}{Journal of Open Hardware}:
\url{https://openhardware.metajnl.com/articles/10.5334/joh.9/}

\hypertarget{grbl}{%
\chapter{Grbl installation and configuration}\label{grbl}}

\hypertarget{overview}{%
\section{Overview}\label{overview}}

CNC motion control is provided by grbl (\url{https://github.com/gnea/grbl}), an open source, embedded, high performance g-code parser. Grbl is written in optimized C and runs directly on an Arduino. This is used in conjunction with the gShield (formerly known as grblshield) which provides the hardware drivers for the stepper motors. Grbl sends out TTL signals on pins A3 and 13 of the Arduino to control coolant flow and spindle direction, respectively. Here these signals are used to remotely control a peristaltic pump.

\hypertarget{flashing-grbl-to-arduino}{%
\section{Flashing Grbl to Arduino}\label{flashing-grbl-to-arduino}}

To flash Grbl to the Arduino you will need a computer with the latest version of the \href{https://www.arduino.cc/en/Main/Software}{Arduino IDE} installed. The following instructions for flashing Grbl to the Arduino are taken from: \url{https://github.com/gnea/grbl/wiki/Compiling-Grbl}

\emph{\textbf{NOTE: Before starting, delete prior Grbl library installations from the Arduino IDE. Otherwise, you'll have compiling issues! On a Mac, Arduino libraries are located in \texttt{\textasciitilde{}/Documents/Arduino/libraries/}. On Windows, it's in \texttt{My\ Documents\textbackslash{}Arduino\textbackslash{}libraries}.}}

\begin{enumerate}
\def\labelenumi{\arabic{enumi}.}
\tightlist
\item
  Download the Grbl source code.
\end{enumerate}

\begin{itemize}
\tightlist
\item
  Open the following page in your web browser: \url{https://github.com/gnea/grbl}
\item
  Click on the \texttt{\textless{}\textgreater{}Code} Tab
\item
  Click the \texttt{Clone\ or\ Download} green button on the Grbl home page.
\item
  Click the \texttt{Download\ ZIP}
\item
  Unzip the download and you'll have a folder called \texttt{grbl-XXX}, where \texttt{XXX} is the release version.
\end{itemize}

\begin{enumerate}
\def\labelenumi{\arabic{enumi}.}
\setcounter{enumi}{1}
\tightlist
\item
  Launch the Arduino IDE (figure \ref{fig:arduinoIDE})
\end{enumerate}

\begin{itemize}
\tightlist
\item
  Make sure you are using the most recent version of the Arduino IDE!
\end{itemize}

\begin{figure}

{\centering  

}

\caption{Arduino IDE}\label{fig:arduinoIDE}
\end{figure}

\begin{enumerate}
\def\labelenumi{\arabic{enumi}.}
\setcounter{enumi}{2}
\tightlist
\item
  Load Grbl into the Arduino IDE as a Library.
\end{enumerate}

\begin{itemize}
\tightlist
\item
  Click the \texttt{Sketch} drop-down menu, navigate to \texttt{Include\ Library} and select \texttt{Add\ .ZIP\ Library}.
\item
  \textbf{IMPORTANT:} Select the \texttt{Grbl} folder \textbf{\emph{inside}} the \texttt{grbl-XXX} folder, which \textbf{only} contains the source files and an example directory (figure \ref{fig:addGrblLib}).
\end{itemize}

\begin{figure}

{\centering  

}

\caption{Loading Grbl library into the Arduino IDE}\label{fig:addGrblLib}
\end{figure}

\begin{itemize}
\tightlist
\item
  If you accidentally select the \texttt{.zip} file or the wrong folder, you will need to navigate to your Arduino library, delete the mistake, and re-do Step 3.
\end{itemize}

\begin{enumerate}
\def\labelenumi{\arabic{enumi}.}
\setcounter{enumi}{3}
\tightlist
\item
  Open the \texttt{GrblUpload} Arduino example.
\end{enumerate}

\begin{itemize}
\tightlist
\item
  Click the \texttt{File} drop-down menu, navigate to \texttt{Examples-\textgreater{}Grbl}, and select \texttt{GrblUpload} (figure \ref{fig:grblUploadFile}).
\end{itemize}

\begin{figure}

{\centering  

}

\caption{GrblUpload example file}\label{fig:grblUploadFile}
\end{figure}

\begin{enumerate}
\def\labelenumi{\arabic{enumi}.}
\setcounter{enumi}{4}
\tightlist
\item
  Compile and upload Grbl to your Arduino.
\end{enumerate}

\begin{itemize}
\tightlist
\item
  Connect your computer directly to the Arduino using the USB cable. Unplug the USB cable from the raspberry pi and plug it into your computer. Remember to reconnect the raspberry pi to the Arduino after you have finished configuring Grbl (figure \ref{fig:laptop2arduino}).
\end{itemize}

\begin{figure}

{\centering  

}

\caption{Laptop connected directly to Arduino}\label{fig:laptop2arduino}
\end{figure}

\begin{itemize}
\tightlist
\item
  Make sure your board is set to the Arduino Uno in the \texttt{Tool-\textgreater{}Board} menu and the serial port is selected correctly in \texttt{Tool-\textgreater{}Serial\ Port}.
\item
  Click the \texttt{Upload}, and Grbl should compile and flash to your Arduino! (Flashing with a programmer also works by using the \texttt{Upload\ Using\ Programmer} menu command.)
\end{itemize}

\hypertarget{check-serial-connection-to-grbl}{%
\section{Check serial connection to Grbl}\label{check-serial-connection-to-grbl}}

\emph{\textbf{NOTE: Before powering up the gShield and motors, check that the actuator carriages for all three axes are approximately centred (figure \ref{fig:actuatorsCentred}). Initially we do not know in which direction the actuator carriages will travel when G-code commands are issued, so positioning each in the middle of its range reduces the risk of collisions with the end stops.}}

\begin{figure}

{\centering  

}

\caption{Actuator carriages centred in preparation for powering-up motors for first time}\label{fig:actuatorsCentred}
\end{figure}

\begin{enumerate}
\def\labelenumi{\arabic{enumi}.}
\tightlist
\item
  Open serial monitor in Arduino IDE
\end{enumerate}

\begin{itemize}
\tightlist
\item
  Click \texttt{Tools} drop-down menu, and select \texttt{Serial\ Monitor}
\end{itemize}

\begin{figure}

{\centering  

}

\caption{Arduino IDE Serial Monitor}\label{fig:serialMonitor}
\end{figure}

\begin{itemize}
\tightlist
\item
  Note that line-ending is set to \texttt{Carriage\ return} and baud rate is set to \texttt{115200} (figure \ref{fig:serialMonitor})
\end{itemize}

\begin{enumerate}
\def\labelenumi{\arabic{enumi}.}
\setcounter{enumi}{1}
\tightlist
\item
  Try issuing a G-code command.
\end{enumerate}

\begin{itemize}
\tightlist
\item
  Type \texttt{?} and hit return.
\item
  This command will report the current position; as we have just started the system up all axes will be at 0.000.
\end{itemize}

\begin{enumerate}
\def\labelenumi{\arabic{enumi}.}
\setcounter{enumi}{2}
\tightlist
\item
  Now try moving actuators
\end{enumerate}

\begin{itemize}
\tightlist
\item
  To move in the x-axis type \texttt{x5} and hit return. Make a note of the direction in which the actuator carriage moves. N.B. this command tells Grbl to move to the x coordinate that is 5 units from the origin, it is not equivalent to telling the robot to move 5 units in the x-axis.
\item
  To move in the opposite direction along the x-axis type \texttt{x-5} and hit return.
\item
  To return to the starting point, use \texttt{x0}
\item
  Repeat for the other axes, replacing the x in the commands with y or z. Make a note of the direction the actuator carriages move with each command.
\end{itemize}

\hypertarget{grbl-configuration}{%
\section{Grbl configuration}\label{grbl-configuration}}

\hypertarget{read-current-configuration}{%
\subsection{Read current configuration}\label{read-current-configuration}}

\begin{itemize}
\tightlist
\item
  The \texttt{\$\$} command will report Grbl's current configuration.
\item
  Descriptions of these settings can be found here: \url{https://github.com/gnea/grbl/wiki/Grbl-v1.1-Configuration}
\item
  These settings will be modified in subsequent steps.
\end{itemize}

\hypertarget{check-directionality-of-each-axis.}{%
\subsection{Check directionality of each axis.}\label{check-directionality-of-each-axis.}}

\begin{figure}

{\centering  

}

\caption{Orientation of robot.}\label{fig:robotOrientation}
\end{figure}

\begin{itemize}
\tightlist
\item
  Orientation of the robot is shown in figure \ref{fig:robotOrientation}.
\item
  At present the origins of all three axes are mid-way along each actuator, because this was the position of the actuator carriages when the system was started.
\item
  Make sure actuator carriages are at their current origin by entering this command: \texttt{x0y0z0}
\item
  Enter the command: \texttt{x5}. The x-axis carriage should move from right to left (orientation of robot is shown in figure \ref{fig:robotOrientation}. If it doesn't, make a note that it will need to be inverted.
\item
  Enter the command: \texttt{y5}. The y-axis carriage should move forwards. If it doesn't, make a note that it will need to be inverted.
\item
  Enter the command: \texttt{z5}. The z-axis carriage should move up. If it doesn't, make a note that it will need to be inverted.
\item
  The direction of the actuators can be inverted using setting \textbf{\$3}, the \href{https://github.com/gnea/grbl/wiki/Grbl-v1.1-Configuration\#3--direction-port-invert-mask}{Direction port invert (mask)}. An appropriate value is selected from table \ref{tab:invertMaskSettings}. For example, to invert the direction of the X and Z axis actuators use the following command: \texttt{\$3=5}
\end{itemize}

\begin{table}

\caption{\label{tab:invertMaskSettings}Masks for direction port inversion.}
\centering
\begin{tabular}[t]{lllll}
\toprule
Setting Value & Mask & Invert X & Invert Y & Invert Z\\
\midrule
0 & 00000000 & N & N & N\\
1 & 00000001 & Y & N & N\\
2 & 00000010 & N & Y & N\\
3 & 00000011 & Y & Y & N\\
4 & 00000100 & N & N & Y\\
\addlinespace
5 & 00000101 & Y & N & Y\\
6 & 00000110 & N & Y & Y\\
7 & 00000111 & Y & Y & Y\\
\bottomrule
\end{tabular}
\end{table}

\hypertarget{activate-hard-limits}{%
\subsection{Activate hard limits}\label{activate-hard-limits}}

Hard limits are a safety feature to prevent the machine from travelling beyond the limits of travel. Grbl monitors the paired limit switches on each axis and if a switch is triggered it will immediately switch off all motors. Hard limits are activated by setting \textbf{\$21} \href{https://github.com/gnea/grbl/wiki/Grbl-v1.1-Configuration\#21---hard-limits-boolean}{hard limits ( boolean)} to 1:

\begin{verbatim}
$21=1
\end{verbatim}

\hypertarget{setup-homing}{%
\subsection{Setup homing}\label{setup-homing}}

The homing cycle is used to set the origin of the Cartesian coordinate system used by the robot. During the homing cycle Grbl moves each actuator in the positive direction until the limit switches are triggered. The homing cycle is activated by setting \textbf{\$22} \href{https://github.com/gnea/grbl/wiki/Grbl-v1.1-Configuration\#22---homing-cycle-boolean}{homing cycle (boolean)} to 1:

\begin{verbatim}
$22=1
\end{verbatim}

Initiate a homing cycle using the following command: \texttt{\$h}. All actuator carriages should move to the origin of their axes. The origin of the Cartesian coordinate system (home) for the robot is shown in figures \ref{fig:xyOrigin} and \ref{fig:zOrigin}

\begin{figure}

{\centering  

}

\caption{Origin of XY coordinate system.}\label{fig:xyOrigin}
\end{figure}

\begin{figure}

{\centering  

}

\caption{Origin of Z axis.}\label{fig:zOrigin}
\end{figure}

We also need to set \textbf{\$24} \href{https://github.com/gnea/grbl/wiki/Grbl-v1.1-Configuration\#24---homing-feed-mmmin}{homing feed rate} and \textbf{\$25} \href{https://github.com/gnea/grbl/wiki/Grbl-v1.1-Configuration\#25---homing-seek-mmmin}{homing seek rate}. Homing seek rate is the initial speed at which Grbl searches for the limit switches. Once it has them, it makes slower approach at the homing feed rate to get a more precise location for machine zero. We will set homing seek rate to 1000 mm/min \texttt{\$24=100} and homing feed rate to 100 mm/min \texttt{\$25=1000}.

At the end of a homing cycle each actuator carriage must be moved off its home limit switch, otherwise the hard limit will be triggered.
The \textbf{\$27} \href{https://github.com/gnea/grbl/wiki/Grbl-v1.1-Configuration\#27---homing-pull-off-mm}{Homing pull-off (mm)} specifies the distance required to clear the limit switches. For our robot we will use a value of 5mm:

\begin{verbatim}
$27=5
\end{verbatim}

\hypertarget{motor-step-size}{%
\subsection{Motor step size}\label{motor-step-size}}

\textbf{\$100}, \textbf{\$101} and \textbf{\$102} define \href{https://github.com/gnea/grbl/wiki/Grbl-v1.1-Configuration\#100-101-and-102--xyz-stepsmm}{{[}X,Y,Z{]} steps/mm}.
Suitable values for our stepper motors are:

\begin{verbatim}
$100=40
$101=40
$102=49.673
\end{verbatim}

If you are using a different type of stepper motor, the step size can be easily calculated by measuring how far each actuator moves in response to a G-code command. For example, we would calculate the step size for the X actuator as follows.

\begin{enumerate}
\def\labelenumi{\arabic{enumi}.}
\tightlist
\item
  Using the serial monitor in the Arduino IDE, issue the following command to \emph{home} the machine:
\end{enumerate}

\begin{verbatim}
$h
\end{verbatim}

\begin{enumerate}
\def\labelenumi{\arabic{enumi}.}
\setcounter{enumi}{1}
\tightlist
\item
  Read the current position of the machine, as reported by the Grbl controller:
\end{enumerate}

\begin{verbatim}
?
\end{verbatim}

After homing the Cartesian coordinates should be zero minus the homing pull-off:
* x = -5
* y = -5
* z = -5

\begin{enumerate}
\def\labelenumi{\arabic{enumi}.}
\setcounter{enumi}{2}
\item
  Make a note of the physical position of the nozzle.
\item
  Issue a g-code command to move to the -100mm position on the x-axis:
\end{enumerate}

\begin{verbatim}
x-100
\end{verbatim}

Keep decreasing the value of x until the x-actuator carriage almost meets the limit switch on the right hand side of the machine. The greater the distance moved, the more precise our calculation of step-size will be.

\begin{enumerate}
\def\labelenumi{\arabic{enumi}.}
\setcounter{enumi}{4}
\tightlist
\item
  Query Grbl's machine coordinates:
\end{enumerate}

\begin{verbatim}
?
\end{verbatim}

\begin{enumerate}
\def\labelenumi{\arabic{enumi}.}
\setcounter{enumi}{5}
\item
  Measure the physical distance travelled along the x-axis in millimetres.
\item
  Find \textbf{\$100}, the currently configured step size for the x-axis:
\end{enumerate}

\begin{verbatim}
$$
\end{verbatim}

\begin{enumerate}
\def\labelenumi{\arabic{enumi}.}
\setcounter{enumi}{7}
\tightlist
\item
  Calculate the correct value for step-size:
\end{enumerate}

\begin{verbatim}
current_step_size = steps/mm in current configuration
grbl_start = start position reported by Grbl controller (mm)
grbl_end = end position reported by Grbl controller (mm)
physical_distance = physical distance moved by actuator (mm)

steps/mm = -(curr_steps_per_mm * (end_pos_grbl-start_pos_grbl)) / physical_distance
\end{verbatim}

\hypertarget{feed-rates-and-acceleration}{%
\subsection{Feed rates and acceleration}\label{feed-rates-and-acceleration}}

\textbf{\$110}, \textbf{\$111} and \textbf{\$112} set the \href{https://github.com/gnea/grbl/wiki/Grbl-v1.1-Configuration\#110-111-and-112--xyz-max-rate-mmmin}{maximum rates (mm/min)} for the X, Y and Z actuators, respectively. We will use the following values:

\begin{verbatim}
$110=5000
$111=5000
$112=2500
\end{verbatim}

\href{https://github.com/gnea/grbl/wiki/Grbl-v1.1-Configuration\#120-121-122--xyz-acceleration-mmsec2}{Acceleration (mm/sec\^{}2)} is set to 50 for all axes:

\begin{verbatim}
$120=50
$121=50
$122=50
\end{verbatim}

\hypertarget{summary-of-settings}{%
\subsection{Summary of settings}\label{summary-of-settings}}

\begin{verbatim}
$0=10
$1=25
$2=0
$3=5
$4=0
$5=0
$6=0
$10=1
$11=0.010
$12=0.002
$13=0
$20=0
$21=1
$22=1
$23=0
$24=100.000
$25=1000.000
$26=250
$27=5.000
$30=1000
$31=0
$32=0
$100=40.000
$101=40.000
$102=49.673
$110=5000.000
$111=5000.000
$112=2500.000
$120=50.000
$121=50.000
$122=50.000
$130=200.000
$131=500.000
$132=200.000
\end{verbatim}

\hypertarget{setting-motor-current}{%
\section{Setting motor current}\label{setting-motor-current}}

The gShield has trimpots for adjusting the motor current of each axis, as shown in figure \ref{fig:gShield}.

\begin{figure}

{\centering  

}

\caption{gShield trimpots}\label{fig:gShield}
\end{figure}

Instructions for setting motor current are provided here:
\url{https://github.com/synthetos/grblShield/wiki/Using-grblShield\#setting-motor-current}

\hypertarget{raspi}{%
\chapter{Raspberry Pi setup}\label{raspi}}

\hypertarget{overview-1}{%
\section{Overview}\label{overview-1}}

The raspberry pi is used to generate, then stream g-code to the Arduino. A small thin-film-transistor (TFT) touchscreen serves as the user interface to the raspberry pi.

\hypertarget{install-image}{%
\section{Install image}\label{install-image}}

\st{The first step is to install Adafruit's custom raspberry pi image on the micro SD card. The custom image is described here:}

\st{\mbox{\texttt{https://learn.adafruit.com/adafruit-pitft-28-inch-resistive-touchscreen-display-raspberry-pi/easy-install}}}

\st{We want the classic version which boots into X by default, rather then the lite version that boots to the command line. The classic version can be downloaded from this link:}

\st{\mbox{\texttt{https://s3.amazonaws.com/adafruit-raspberry-pi/2016-10-18-pitft-28r.zip}}}

Adafruit's custom raspberry pi image is no longer available. I have created an image (pitft.img) based on Adafruit's original that is preconfigured for use with the robot. It can be downloaded from:

\url{https://zenodo.org/records/10534021}

Instructions on installing images on SD cards can be found here:

\url{https://www.raspberrypi.org/documentation/installation/installing-images/}

\hypertarget{network-configuration}{%
\section{Network configuration}\label{network-configuration}}

The small screen of the pitft makes using most applications quite tricky. Therefore the first thing we should do after installing the image is configure networking, so that we can access the raspberry pi remotely using ssh.

To set a static IP address for the ethernet adapter, edit the following lines of \texttt{/etc/dhcpcd.conf}:

\begin{verbatim}
interface eth0

static ip_address=192.168.1.3/24
static routers=192.168.1.254
static domain_name_servers=192.168.1.254
\end{verbatim}

\textbf{ip\_address}, \textbf{routers} and \textbf{domain\_name\_servers} should be set to values appropriate for your network.

To raspberry pi can then be accessed using ssh, \emph{e.g.}:

\begin{verbatim}
  ssh pi@192.168.1.3
\end{verbatim}

The default password for the \textbf{pi} user account is \textbf{raspberry}

\hypertarget{install-minicom}{%
\section{Install minicom}\label{install-minicom}}

\emph{N.B. Minicom is pre-installed on my pitft.img}

Minicom is useful for manual control of the robot and for editing grbl settings.

To install minicom run these two commands:

\begin{verbatim}
sudo apt-get update
sudo apt-get install minicom
\end{verbatim}

Before we can use minicom we need to enable serial:

\begin{verbatim}
sudo nano /boot/config.txt
\end{verbatim}

Change the last line of this file from

\begin{verbatim}
enable_uart=0
\end{verbatim}

to

\begin{verbatim}
enable_uart=1
\end{verbatim}

If you have not already done so, reconnect the raspberry pi to the arduino using the USB cable. To use minicom to connect to the grbl controller running on the arduino, use:

\begin{verbatim}
sudo minicom -D /dev/ttyACM0 -b115200
\end{verbatim}

\hypertarget{expand-filesystem}{%
\section{Expand filesystem}\label{expand-filesystem}}

Expand filesystem on micro SD card:

\begin{verbatim}
    sudo raspi-config
    (expand filesystem)
    sudo reboot
\end{verbatim}

\hypertarget{installScripts}{%
\section{Install python scripts}\label{installScripts}}

\emph{N.B. The python scripts are pre-installed on my pitft.img}

Make sure you are in pi's home directory:

\begin{verbatim}
cd
\end{verbatim}

Download and unpack robot.tar.gz

\begin{verbatim}
curl -O https://raw.githubusercontent.com/WaylandM/fly-food-robot/master/raspberrypi/robot.tar.gz
tar xzvf robot.tar.gz
\end{verbatim}

The \textbf{robot} directory contains two subdirectories: \textbf{nc} (g-code scripts) and \textbf{py} (python scripts).

To automatically launch the robot GUI when the raspberry pi starts up, we need to edit the autostart file for the pi user:

\begin{verbatim}
sudo nano /home/pi/.config/lxsession/LXDE-pi/autostart
\end{verbatim}

Add the following line to autostart:

\begin{verbatim}
@/home/pi/robot/py/fly_gui.py
\end{verbatim}

\hypertarget{startup}{%
\chapter{System start-up}\label{startup}}

\hypertarget{attach-norprene-tubing}{%
\section{Attach Norprene tubing}\label{attach-norprene-tubing}}

\begin{enumerate}
\def\labelenumi{\arabic{enumi}.}
\tightlist
\item
  Attach the nozzle end of the Norprene tubing to the holder on the Z-axis actuator using releasable cable ties (figure \ref{fig:attachNozzle}).
\end{enumerate}

\begin{figure}

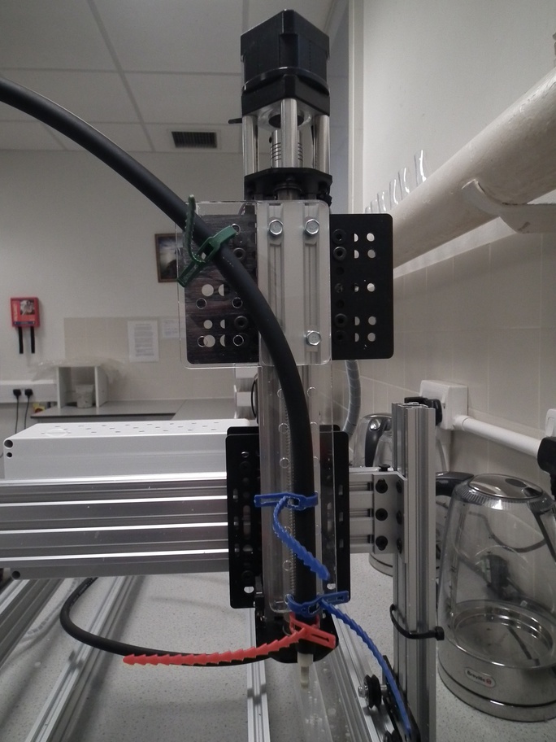
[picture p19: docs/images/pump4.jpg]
{\centering  

}

\caption{Attachment of nozzle end of tubing to the Z-axis actuator.}\label{fig:attachNozzle}
\end{figure}

\begin{enumerate}
\def\labelenumi{\arabic{enumi}.}
\setcounter{enumi}{1}
\tightlist
\item
  Attach the Masterflex Norprene tubing to the right-hand side vertical post using a releasable cable tie. Ensure there is a large loop in the tubing between this attachment point and the nozzle so that the x-axis actuator can move freely (figure \ref{fig:tubingPost})
\end{enumerate}

\begin{figure}

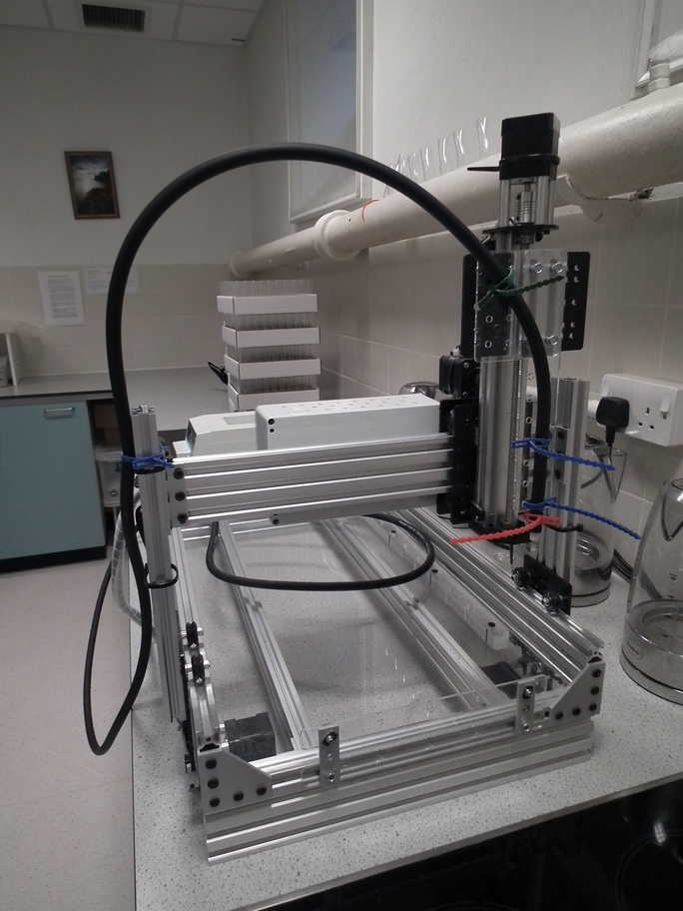
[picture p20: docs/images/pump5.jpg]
{\centering  

}

\caption{Attachment of Norprene tubing to the right-hand side vertical post.}\label{fig:tubingPost}
\end{figure}

\begin{enumerate}
\def\labelenumi{\arabic{enumi}.}
\setcounter{enumi}{2}
\tightlist
\item
  Feed the tubing through the peristaltic pump (figure \ref{fig:tubingPump}) and into your vat of fly food (figure \ref{fig:flyFoodVat}).
\end{enumerate}

\begin{figure}

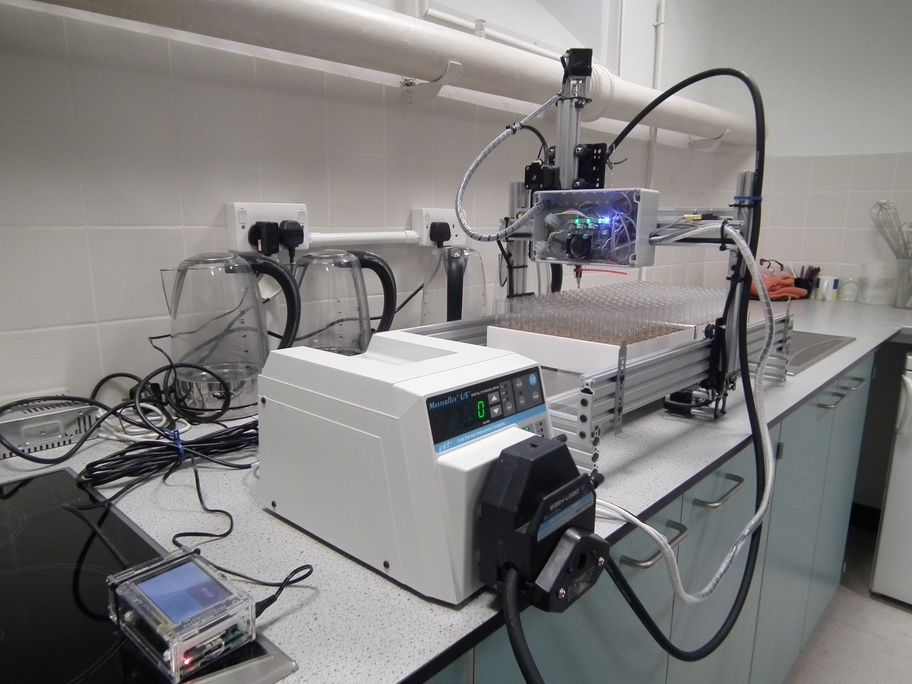
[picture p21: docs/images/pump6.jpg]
{\centering  

}

\caption{Norprene tubing passing through peristaltic pump.}\label{fig:tubingPump}
\end{figure}

\begin{figure}

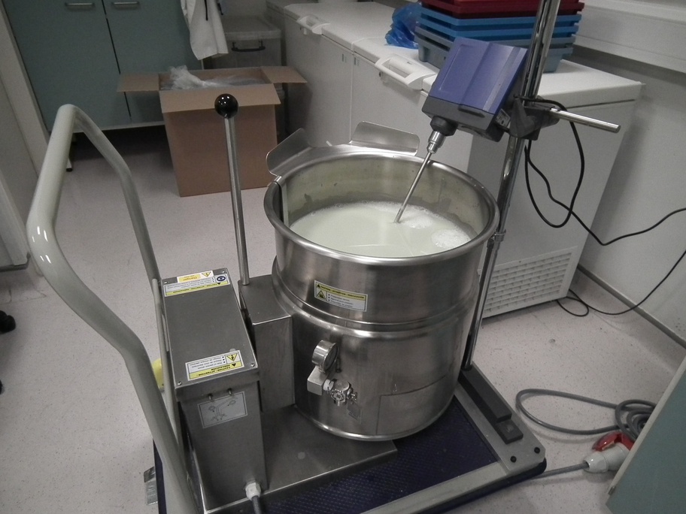
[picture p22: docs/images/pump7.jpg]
{\centering  

}

\caption{Vat of fly food.}\label{fig:flyFoodVat}
\end{figure}

\hypertarget{switch-on-all-devices}{%
\section{Switch on all devices}\label{switch-on-all-devices}}

\begin{itemize}
\tightlist
\item
  power supply unit for gShield and motors
\item
  raspberry pi
\item
  peristaltic pump
\end{itemize}

\hypertarget{prime-pump}{%
\section{Prime pump}\label{prime-pump}}

\begin{itemize}
\tightlist
\item
  Position a beaker under the nozzle (figure \ref{fig:primeBeaker}).
\item
  Press and hold the prime button on the front of the peristaltic pump until a continuous stream of fly food is pumped into the beaker (figure \ref{fig:primeButton})
\end{itemize}

\begin{figure}

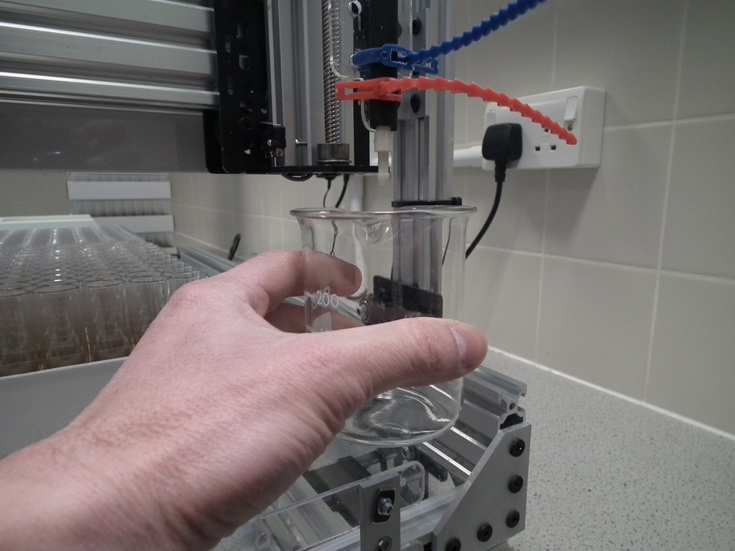
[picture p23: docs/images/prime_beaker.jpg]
{\centering  

}

\caption{Positioning of beaker under nozzle to collect fly food expelled during priming of peristaltic pump.}\label{fig:primeBeaker}
\end{figure}

\begin{figure}

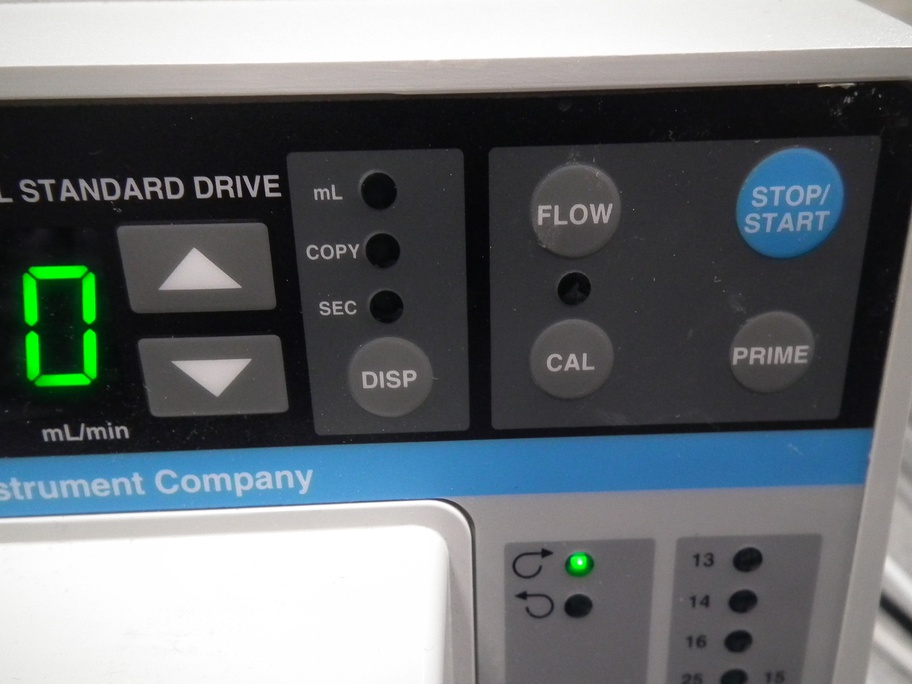
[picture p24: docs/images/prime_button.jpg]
{\centering  

}

\caption{Prime button on peristaltic pump.}\label{fig:primeButton}
\end{figure}

\hypertarget{gcode}{%
\chapter{Program robot to fill vials}\label{gcode}}

\hypertarget{overview-2}{%
\section{Overview}\label{overview-2}}

The movement of the robot is programmed in \href{https://en.wikipedia.org/wiki/G-code}{G-code}. We only need nine G-code commands to control the robot (table \ref{tab:gCodes}).

\begin{table}

\caption{\label{tab:gCodes}G-code commands used to control robot.}
\centering
\begin{tabular}[t]{ll}
\toprule
Code & Description\\
\midrule
x & absolute position of x-axis\\
y & absolute position of y-axis\\
z & absolute position of z-axis\\
g4 & dwell time (control parameter p specifies seconds)\\
m3 & set pump rotation to clockwise\\
\addlinespace
m4 & set pump rotation to counter clockwise\\
m8 & start pump\\
m9 & stop pump\\
\$h & initiate homing cycle\\
\bottomrule
\end{tabular}
\end{table}

A G-code program for filling vials of food could be created manually, by listing the necessary commands sequentially in a text file. However, this would be laborious and error prone. If the size of the boxes of vials are known, the G-code can be programmatically generated.

\hypertarget{loadBoxes}{%
\section{Load boxes}\label{loadBoxes}}

\begin{figure}

{\centering   

}

\caption{Loading boxes of vials.}\label{fig:loadBoxes2}
\end{figure}

Load boxes onto the platform of the robot (figure \ref{fig:loadBoxes2}).
* The first box should be flush with the fence and the guide rail.
* The second box should be flush with the first and the guide rail.
* The boxes we are using have a pair of double-thickness side-walls and a pair of single-thickness side-walls. The pairs are on opposite sides of the box. With this type of box it is important to note the orientation of the boxes when the Cartesian coordinates of the vials are determined, because the same orientation must be used when filling vials with food. We load the boxes with a double-thickness side-wall facing forwards.

\hypertarget{boxCoordinates}{%
\section{Determine box coordinates}\label{boxCoordinates}}

We need to determine the Cartesian coordinates of vials in diagonally opposite corners of each box.

\begin{enumerate}
\def\labelenumi{\arabic{enumi}.}
\tightlist
\item
  Login to raspberry pi using ssh. My raspberry pi has the IP address 192.168.1.3 and so I would use:
\end{enumerate}

\begin{itemize}
\tightlist
\item
  \texttt{ssh\ pi@192.168.1.3}
\item
  Default password for the \textbf{pi} user account is `raspberry'.
\end{itemize}

\begin{enumerate}
\def\labelenumi{\arabic{enumi}.}
\setcounter{enumi}{1}
\tightlist
\item
  Use minicom to connect to the Grbl controller running on the Arduino, so that we can interactively control the robot from the command line:
\end{enumerate}

\begin{verbatim}
sudo minicom -D /dev/ttyACM0 -b115200
\end{verbatim}

\begin{enumerate}
\def\labelenumi{\arabic{enumi}.}
\setcounter{enumi}{2}
\tightlist
\item
  Make sure nozzle is at ** home ** position by issuing homing command:
\end{enumerate}

\begin{verbatim}
$h
\end{verbatim}

\begin{enumerate}
\def\labelenumi{\arabic{enumi}.}
\setcounter{enumi}{3}
\tightlist
\item
  First we will determine the Cartesian coordinates of the vial in the front left corner of the first box.
\end{enumerate}

\begin{itemize}
\tightlist
\item
  Make small movements in X and Y until the nozzle is centred over this vial, \emph{e.g.}:
\end{itemize}

\begin{verbatim}
x-8 y-8
\end{verbatim}

\begin{itemize}
\tightlist
\item
  Lower the nozzle in small increments until it is just 2-3mm above the the top of the vial (figure \ref{fig:box1FrontLeft}), \emph{e.g.}:
\end{itemize}

\begin{verbatim}
z-20
\end{verbatim}

\begin{itemize}
\tightlist
\item
  Query the current X, Y and Z coordinates by issuing the following command:
\end{itemize}

\begin{verbatim}
?
\end{verbatim}

Make a note of all three coordinates.

\begin{figure}

{\centering  

}

\caption{Nozzle positioned over the front left vial in box 1.}\label{fig:box1FrontLeft}
\end{figure}

\begin{enumerate}
\def\labelenumi{\arabic{enumi}.}
\setcounter{enumi}{4}
\tightlist
\item
  Issue G-code commands to move the nozzle laterally until it is over the back right vial of the first box (figure \ref{fig:box1BackRight}).
\end{enumerate}

\begin{figure}

{\centering  

}

\caption{Nozzle positioned over the back right vial in box 1.}\label{fig:box1BackRight}
\end{figure}

\begin{itemize}
\tightlist
\item
  Use \texttt{?} command to query nozzle position, and make a note of the X and Y coordinates:
\end{itemize}

\begin{enumerate}
\def\labelenumi{\arabic{enumi}.}
\setcounter{enumi}{5}
\tightlist
\item
  Move the nozzle laterally until it is over the front left vial of the second box (figure \ref{fig:box2FrontLeft}), then record X and Y coordinates.
\end{enumerate}

\begin{figure}

{\centering  

}

\caption{Nozzle positioned over the front left vial in box 2.}\label{fig:box2FrontLeft}
\end{figure}

\begin{enumerate}
\def\labelenumi{\arabic{enumi}.}
\setcounter{enumi}{6}
\tightlist
\item
  Finally determine the X and Y coordinates of the back right vial in the second box (figure \ref{fig:box2BackRight}).
\end{enumerate}

\begin{figure}

{\centering  

}

\caption{Nozzle positioned over the back right vial in box 2.}\label{fig:box2BackRight}
\end{figure}

\hypertarget{calibratePump}{%
\section{Calibrate pump}\label{calibratePump}}

The peristaltic pump is started and stopped using the \texttt{m8} and \texttt{m9} G-code commands, respectively (table \ref{tab:gCodes}). To maximize speed, the pump will be run at its maximum flow rate of 30ml/second. In our fly facility, we add 9ml of food to each vial, therefore based on the maximum flow rate, we should only need to run the pump for 0.3 seconds to dispense 9ml of food. However, there is latency in the system and the pump does not reach its maximum flow rate instantaneously on activation. Therefore, it is important to determine the \emph{fill time} empirically. We do this by programming the robot to test fill a single box of vials using a range of \emph{fill times}. The \textbf{calibrate\_pump.py} script downloaded to the Raspberry Pi in stage \ref{installScripts} can be used to generate the appropriate G-code program.

\begin{enumerate}
\def\labelenumi{\arabic{enumi}.}
\tightlist
\item
  Open \textbf{calibrate\_pump.py} for editing:
\end{enumerate}

\begin{verbatim}
sudo nano /home/pi/robot/py/calibrate_pump.py
\end{verbatim}

\begin{enumerate}
\def\labelenumi{\arabic{enumi}.}
\setcounter{enumi}{1}
\tightlist
\item
  Near the top of the file (line 32 onwards) are various settings to be modified:
\end{enumerate}

\begin{verbatim}

# SETTINGS

# filename
filename = '/home/pi/robot/nc/calibrate_pump.nc'

# home/datum + homing pull-off (mm) (value of Grbl setting $27)
x_home = -5
y_home = -5
z_home = -5

# z value providing minimal clearance between nozzle and top of vials
z_fill = -62 

# peristaltic pump settings
min_fill_time = 0.3
max_fill_time = 0.6
# pause to allow for drips before moving to next vial
drip_pause = 0.1 

# vial coordinates (x,y)
frontLeft = (-8,-14)
backRight = (-236,-240)

nrows=10
ncols=10
\end{verbatim}

\begin{itemize}
\tightlist
\item
  The \textbf{filename} is the full path to the G-code file that will be generated by the python script.
\item
  The parameters \textbf{x\_home, y\_home} and \textbf{z\_home} are the Cartesian coordinates of the home position (\emph{i.e.} home/datum + homing pull-off (mm)).
\item
  Modify \textbf{z\_fill} to the appropriate nozzle height for filling vials (this was determined in step 5 of section \ref{boxCoordinates}).
\item
  The \textbf{min\_fill\_time} should be set to our estimate of \emph{fill time} based on the pump's specified flow rate. We will set \textbf{max\_fill\_time} to twice the value of \textbf{min\_fill\_time}.
\item
  The vial coordinates (\textbf{frontLeft} and \textbf{frontRight}) are those determined for the front left and back right vials in the first box (refer to steps 5 and 6 of section \ref{boxCoordinates}).
\item
  Our boxes have ten rows, each containing ten vials, so we set \textbf{nrows} and \textbf{ncols} to 10.
\end{itemize}

\begin{enumerate}
\def\labelenumi{\arabic{enumi}.}
\setcounter{enumi}{2}
\tightlist
\item
  After editing the settings in \textbf{calibrate\_pump.py}, run the script to generate a G-code program:
\end{enumerate}

\begin{verbatim}
./robot/py/calibrate_pump.py
\end{verbatim}

This will generate a G-code program: \textbf{/home/pi/robot/nc/calibrate\_pump.nc} which will iteratively increase the fill time for each successive row of vials. The \textbf{min\_fill\_time} will be used for the first row of vials and the fill time will be increased by (\textbf{max\_fill\_time} - \textbf{min\_fill\_time}) / (\textbf{nrows} - 1.0) for each successive row (\emph{e.g.} table \ref{tab:calibrationFillTimes}). Note that the fill times are rounded to the nearest 100th of a second. The fill time for each row is listed in the comments at the top of the \textbf{/home/pi/robot/nc/calibrate\_pump.nc} file; to view this information run:

\begin{verbatim}
head -n12 ~/robot/nc/calibrate_pump.nc
\end{verbatim}

\begin{table}

\caption{\label{tab:calibrationFillTimes}Example calibration fill times.}
\centering
\begin{tabular}[t]{rr}
\toprule
Box Row & Fill Time\\
\midrule
1 & 0.30\\
2 & 0.33\\
3 & 0.37\\
4 & 0.40\\
5 & 0.43\\
\addlinespace
6 & 0.47\\
7 & 0.50\\
8 & 0.53\\
9 & 0.57\\
10 & 0.60\\
\bottomrule
\end{tabular}
\end{table}

\begin{enumerate}
\def\labelenumi{\arabic{enumi}.}
\setcounter{enumi}{3}
\tightlist
\item
  Send the G-code pump-calibration program to the Grbl controller
  \textbf{/home/pi/robot/py/stream2.py} can be used to stream a text file of G-code commands to Grbl:
\end{enumerate}

\begin{verbatim}
./robot/py/stream2.py robot/nc/calibrate_pump.nc /dev/ttyACM0
\end{verbatim}

Once the robot has completed the calibration run and returned the nozzle to the home position, inspect the fill level in each row of vials. Identify the row in which vials are filled with the desired volume of food and then refer to the \textbf{/home/pi/robot/calibrate\_pump.nc} file to find out the fill time used for that particular row.

\hypertarget{generate-programs}{%
\section{Generate programs}\label{generate-programs}}

Once the pump has been calibrated we are ready to generate the G-code instructions for the routine filling of vials. The \textbf{fill\_boxes.py} script downloaded to the Raspberry Pi in stage \ref{installScripts} is used to generate two G-code programs:

\begin{itemize}
\tightlist
\item
  \textbf{1\_box.nc} - fill one box of vials
\item
  \textbf{2\_boxes.nc} - fill two boxes of vials
\end{itemize}

\begin{enumerate}
\def\labelenumi{\arabic{enumi}.}
\tightlist
\item
  Open \textbf{fill\_boxes.py} for editing:
\end{enumerate}

\begin{verbatim}
sudo nano /home/pi/robot/py/fill_boxes.py
\end{verbatim}

\begin{enumerate}
\def\labelenumi{\arabic{enumi}.}
\setcounter{enumi}{1}
\tightlist
\item
  Near the top of the file (line 32 onwards) are various settings to be modified:
\end{enumerate}

\begin{verbatim}

# SETTINGS
# modify values of variables in this section to match your system

# filenames
filename1Box = '/home/pi/robot/nc/1_box.nc'
filename2Boxes = '/home/pi/robot/nc/2_boxes.nc'

# home/datum + homing pull-off (mm) (value of Grbl setting $27)
x_home = -5
y_home = -5
z_home = -5

# z value providing minimal clearance between nozzle and top of vials
z_fill = -62 

# peristaltic pump settings
fill_time = 0.43
# pause to allow for drips before moving to next vial
drip_pause = 0.1 

# vial coordinates (x,y)
box1FrontLeft = (-8,-14)
box1BackRight = (-236,-240)
box2FrontLeft = (-8,-286)
box2BackRight = (-236,-513)

nrows=10
ncols=10
nVials=nrows*ncols
\end{verbatim}

\begin{itemize}
\tightlist
\item
  \textbf{filename1Box} and \textbf{filename2Boxes} specify the filename and full path to the two G-code programs that will be generated. You should not need to modify these values. The GUI script (\textbf{/home/pi/robot/py/fly\_gui.py}) expects the two programs to have the default names and paths; if you alter the names or paths of these files, you will need to edit the GUI script.
\item
  The parameters \textbf{x\_home, y\_home} and \textbf{z\_home} are the Cartesian coordinates of the home position (\emph{i.e.} home/datum + homing pull-off (mm)).
\item
  Modify \textbf{z\_fill} to the appropriate nozzle height for filling vials (this was determined in step 5 of section \ref{boxCoordinates}).
\item
  \textbf{fill\_time} was determined in the previous section \ref{calibratePump}.
\item
  The default value of \textbf{drip\_pause} should be appropriate for most systems.
\item
  The vial coordinates (\textbf{box1FrontLeft}, \textbf{box1BackRight}, \textbf{box2FrontLeft} and \textbf{box2BackRight}) were determined in section \ref{boxCoordinates}.
\item
  Our boxes have ten rows, each containing ten vials, so we set \textbf{nrows} and \textbf{ncols} to 10.
\end{itemize}

\begin{enumerate}
\def\labelenumi{\arabic{enumi}.}
\setcounter{enumi}{2}
\tightlist
\item
  After editing the settings in \textbf{fill\_boxes.py}, run the script to generate the two G-code programs:
\end{enumerate}

\begin{verbatim}
./robot/py/fill_boxes.py
\end{verbatim}

\hypertarget{operation}{%
\chapter{Routine operation}\label{operation}}

\hypertarget{prepare-system}{%
\section{Prepare system}\label{prepare-system}}

Instructions for starting the system are provided in chapter \ref{startup}.

\hypertarget{fill-boxes}{%
\section{Fill boxes}\label{fill-boxes}}

Load boxes onto platform as described in section \ref{loadBoxes}.

From the touchscreen menu select \textbf{1 Box} or \textbf{2 Boxes} depending on the number of boxes on the platform (figure \ref{fig:touchscreen}). The robot will \textbf{home} to zero the cartesian coordinate system, and then commence filling the vials.

\begin{figure}

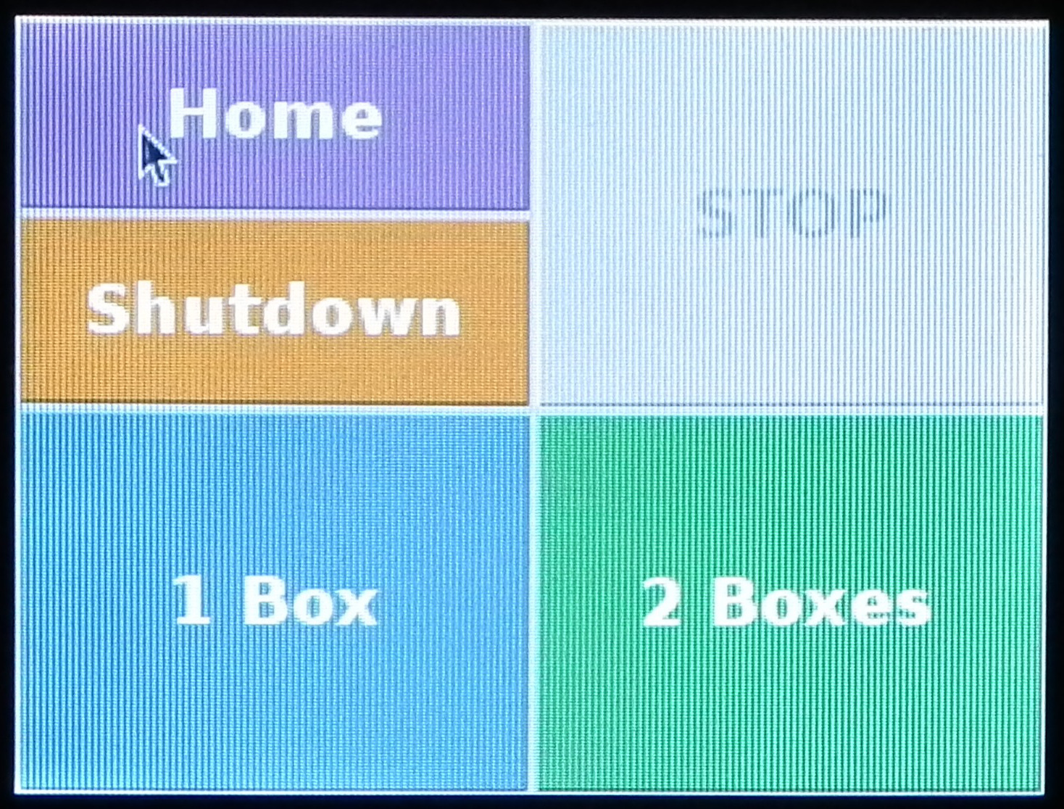
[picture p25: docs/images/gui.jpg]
{\centering  

}

\caption{Touchscreen interface.}\label{fig:touchscreen}
\end{figure}

During filling the robot can be stopped by clicking on the \textbf{Stop} button (figure \ref{fig:stopRobot}).

\begin{figure}

{\centering  

}

\caption{Appearance of touchscreen interface when a job is running.}\label{fig:stopRobot}
\end{figure}

\hypertarget{shutdown}{%
\section{Shutdown}\label{shutdown}}

\begin{itemize}
\tightlist
\item
  The raspberry pi should be shutdown using the \textbf{shutdown} button on the touchscreen.
\item
  The Norprene tubing should be removed from the vat of fly food, then any food remaining in the tubing can be expelled by pressing and holding the \textbf{prime} button on the peristaltic pump. Ensure there is a receptacle under the nozzle to catch the expelled fly food. The Norprene tubing should be removed from the robot for cleaning/sterilization.
\item
  All devices (raspberry pi, power supply unit for gShield and motors, and peristaltic pump) should be switched off.
\item
  The robot can be wiped clean if necessary using a damp cloth. The platform can be removed for thorough cleaning.
\end{itemize}

  \bibliography{book.bib,packages.bib}

\end{document}

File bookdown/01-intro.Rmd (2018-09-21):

# Introduction {#intro}

The fruit fly, *Drosophila melanogaster*, is one of the most important model organisms in biological research. Maintaining stocks of fruit flies in the laboratory is labour-intensive. One task which lends itself to automation is the production of the vials of food in which the flies are reared. Fly facilities typically have to generate several thousand vials of fly food each week to sustain their fly stocks. The system presented here combines a Cartesian coordinate robot with a peristaltic pump (Figure \@ref(fig:architecture)). The design of the robot is based on the Routy CNC Router created by Mark Carew (http://openbuilds.org/builds/routy-cnc-router-v-slot-belt-pinion.101/), and uses belt and pully actuators for the X and Y axes, and a leadscrew actuator for the Z axis. CNC motion and operation of the peristaltic pump are controlled by grbl (https://github.com/gnea/grbl), an open source, embedded, high performance g-code parser. Grbl is written in optimized C and runs directly on an Arduino. A Raspberry Pi is used to generate and stream G-code instructions to Grbl. A touch screen on the Raspberry Pi provides a graphical user interface to the system. The system has capacity to fill two boxes of fly food vials at a time.  Instructions for building the hardware are available on [DocuBricks](http://docubricks.com/viewer.jsp?id=8652757760093769728).

```{r architecture, echo=FALSE, out.width='75%', fig.align='center', fig.cap="System architecture."}
knitr::include_graphics("images/system_architecture.svg")
```
 
Software installation and configuration on the Arduino and raspberry pi are detailed in chapters \@ref(grbl) and \@ref(raspi). Chapter \@ref(gcode) explains how to program the robot to fill vials of fly food. Instructions for the routine use of the robot are provided in chapter \@ref(operation). To see a video of the robot in action, go to:

https://doi.org/10.6084/m9.figshare.5175223.v1
 
An article providing an overview of this project has been published in the [Journal of Open Hardware](https://openhardware.metajnl.com/):
https://openhardware.metajnl.com/articles/10.5334/joh.9/

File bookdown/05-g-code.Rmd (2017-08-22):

# Program robot to fill vials {#gcode}

<!--
# need 8-9 ml
# pump speed 1800ml/min
# ml/s = 1800/60 = 30
# fill time = 0.3
-->

<!--
ssh pi@192.168.1.3

sudo minicom -D /dev/ttyACM0 -b115200

?<Idle|MPos:-5.000,-5.000,-4.993|FS:0,0|Ov:100,100,100>

x-10 y-10 z-10
ok
?<Idle|MPos:-10.000,-10.000,-10.005|FS:0,0>

x-20 y-20 z-30
ok
?<Idle|MPos:-20.000,-20.000,-29.996|FS:0,0>

x-8 y-14 z-62
ok
?<Idle|MPos:-8.000,-14.000,-62.006|FS:0,0>

./robot/py/calibrate_pump.py

./robot/py/stream2.py robot/nc/calibrate_pump.nc /dev/ttyACM0

./robot/py/fill_boxes.py

-->

## Overview
The movement of the robot is programmed in [G-code](https://en.wikipedia.org/wiki/G-code). We only need nine G-code commands to control the robot (table \@ref(tab:gCodes)).

```{r gCodes, echo=FALSE}
command <- c("x", "y", "z", "g4",  "m3", "m4", "m8", "m9", "$h")
description <- c("absolute position of x-axis", "absolute position of y-axis", "absolute position of z-axis", "dwell time (control parameter p specifies seconds)", "set pump rotation to clockwise", "set pump rotation to counter clockwise", "start pump", "stop pump", "initiate homing cycle")
commandDescriptions <- as.data.frame(cbind(command,description))
names(commandDescriptions) <- c("Code", "Description")
knitr::kable(
  commandDescriptions, booktabs = TRUE,
  caption = 'G-code commands used to control robot.'
)
```

A G-code program for filling vials of food could be created manually, by listing the necessary commands sequentially in a text file.  However, this would be laborious and error prone. If the size of the boxes of vials are known, the G-code can be programmatically generated. 

## Load boxes {#loadBoxes}

```{r loadBoxes2, echo = F, fig.cap = 'Loading boxes of vials.', fig.align = 'center', fig.show='hold', out.width = '50%'}
knitr::include_graphics(c("images/one_box_loaded.jpg", "images/two_boxes_loaded.jpg"))
```

Load boxes onto the platform of the robot (figure \@ref(fig:loadBoxes2)).
 * The first box should be flush with the fence and the guide rail.
 * The second box should be flush with the first and the guide rail.
 * The boxes we are using have a pair of double-thickness side-walls and a pair of single-thickness side-walls. The pairs are on opposite sides of the box. With this type of box it is important to note the orientation of the boxes when the Cartesian coordinates of the vials are determined, because the same orientation must be used when filling vials with food. We load the boxes with a double-thickness side-wall facing forwards.

## Determine box coordinates {#boxCoordinates}

We need to determine the Cartesian coordinates of vials in diagonally opposite corners of each box.

1. Login to raspberry pi using ssh. My raspberry pi has the IP address 192.168.1.3 and so I would use:
* ``` ssh pi@192.168.1.3 ```
* Default password for the **pi** user account is 'raspberry'.

2. Use minicom to connect to the Grbl controller running on the Arduino, so that we can interactively control the robot from the command line:
```
sudo minicom -D /dev/ttyACM0 -b115200
```

3. Make sure nozzle is at ** home ** position by issuing homing command:
```
$h
```

4. First we will determine the Cartesian coordinates of the vial in the front left corner of the first box.

* Make small movements in X and Y until the nozzle is centred over this vial, *e.g.*:
```
x-8 y-8
```

* Lower the nozzle in small increments until it is just 2-3mm above the the top of the vial (figure \@ref(fig:box1FrontLeft)), *e.g.*:
```
z-20
```

* Query the current X, Y and Z coordinates by issuing the following command:
```
?
```
Make a note of all three coordinates. 

```{r box1FrontLeft, echo = F, fig.cap = 'Nozzle positioned over the front left vial in box 1.', fig.align = 'center', fig.show='hold', out.width = '50%'}
knitr::include_graphics("images/box1_first_vial.jpg")
```

5. Issue G-code commands to move the nozzle laterally until it is over the back right vial of the first box (figure \@ref(fig:box1BackRight)).

```{r box1BackRight, echo = F, fig.cap = 'Nozzle positioned over the back right vial in box 1.', fig.align = 'center', fig.show='hold', out.width = '50%'}
knitr::include_graphics("images/box1_last_vial.jpg")
```
* Use ```?``` command to query nozzle position, and make a note of the X and Y coordinates:

6. Move the nozzle laterally until it is over the front left vial of the second box (figure \@ref(fig:box2FrontLeft)), then record X and Y coordinates.

```{r box2FrontLeft, echo = F, fig.cap = 'Nozzle positioned over the front left vial in box 2.', fig.align = 'center', fig.show='hold', out.width = '50%'}
knitr::include_graphics("images/box2_first_vial.jpg")
```

7. Finally determine the X and Y coordinates of the back right vial in the second box (figure \@ref(fig:box2BackRight)).

```{r box2BackRight, echo = F, fig.cap = 'Nozzle positioned over the back right vial in box 2.', fig.align = 'center', fig.show='hold', out.width = '50%'}
knitr::include_graphics("images/box2_last_vial.jpg")
```

## Calibrate pump {#calibratePump}
<!--
# need 8-9 ml
# pump speed 1800ml/min
# ml/s = 1800/60 = 30
# fill time = 0.3
-->
The peristaltic pump is started and stopped using the ```m8``` and ```m9``` G-code commands, respectively (table \@ref(tab:gCodes)). To maximize speed, the pump will be run at its maximum flow rate of 30ml/second. In our fly facility, we add 9ml of food to each vial, therefore based on the maximum flow rate, we should only need to run the pump for 0.3 seconds to dispense 9ml of food. However, there is latency in the system and the pump does not reach its maximum flow rate instantaneously on activation. Therefore, it is important to determine the *fill time* empirically. We do this by programming the robot to test fill a single box of vials using a range of *fill times*. The **calibrate_pump.py** script downloaded to the Raspberry Pi in stage \@ref(installScripts) can be used to generate the appropriate G-code program. 

1. Open **calibrate_pump.py** for editing:
```
sudo nano /home/pi/robot/py/calibrate_pump.py
```

2. Near the top of the file (line 32 onwards) are various settings to be modified:

``` 

# SETTINGS

# filename
filename = '/home/pi/robot/nc/calibrate_pump.nc'

# home/datum + homing pull-off (mm) (value of Grbl setting $27)
x_home = -5
y_home = -5
z_home = -5

# z value providing minimal clearance between nozzle and top of vials
z_fill = -62 

# peristaltic pump settings
min_fill_time = 0.3
max_fill_time = 0.6
# pause to allow for drips before moving to next vial
drip_pause = 0.1 

# vial coordinates (x,y)
frontLeft = (-8,-14)
backRight = (-236,-240)

nrows=10
ncols=10
```

* The **filename** is the full path to the G-code file that will be generated by the python script. 
* The parameters **x_home, y_home** and **z_home** are the Cartesian coordinates of the home position (*i.e.* home/datum + homing pull-off (mm)). 
* Modify **z_fill** to the appropriate nozzle height for filling vials (this was determined in step 5 of section \@ref(boxCoordinates)). 
* The **min_fill_time** should be set to our estimate of *fill time* based on the pump's specified flow rate. We will set **max_fill_time** to twice the value of **min_fill_time**.
* The vial coordinates (**frontLeft** and **frontRight**) are those determined for the front left and back right vials in the first box (refer to steps 5 and 6 of section \@ref(boxCoordinates)). 
* Our boxes have ten rows, each containing ten vials, so we set **nrows** and **ncols** to 10.

3. After editing the settings in **calibrate_pump.py**, run the script to generate a G-code program:
```
./robot/py/calibrate_pump.py
```
This will generate a G-code program: **/home/pi/robot/nc/calibrate_pump.nc** which will iteratively increase the fill time for each successive row of vials. The **min_fill_time** will be used for the first row of vials and the fill time will be increased by (**max_fill_time** - **min_fill_time**) / (**nrows** - 1.0) for each successive row (*e.g.* table \@ref(tab:calibrationFillTimes)). Note that the fill times are rounded to the nearest 100th of a second. The fill time for each row is listed in the comments at the top of the **/home/pi/robot/nc/calibrate_pump.nc** file; to view this information run:
```
head -n12 ~/robot/nc/calibrate_pump.nc
```

```{r calibrationFillTimes, echo=FALSE}
boxRow <- seq(1,10)
fillTime <- c(0.3, 0.33, 0.37, 0.4, 0.43, 0.47, 0.5, 0.53, 0.57, 0.6)
fillTimeTable <- as.data.frame(cbind(boxRow,fillTime))
names(fillTimeTable) <- c("Box Row", "Fill Time")
knitr::kable(
  fillTimeTable, booktabs = TRUE,
  caption = 'Example calibration fill times.'
)
```

4. Send the G-code pump-calibration program to the Grbl controller
**/home/pi/robot/py/stream2.py** can be used to stream a text file of G-code commands to Grbl: 
```
./robot/py/stream2.py robot/nc/calibrate_pump.nc /dev/ttyACM0
```
Once the robot has completed the calibration run and returned the nozzle to the home position, inspect the fill level in each row of vials. Identify the row in which vials are filled with the desired volume of food and then refer to the **/home/pi/robot/calibrate_pump.nc** file to find out the fill time used for that particular row.

## Generate programs
Once the pump has been calibrated we are ready to generate the G-code instructions for the routine filling of vials. The **fill_boxes.py** script downloaded to the Raspberry Pi in stage \@ref(installScripts) is used to generate two G-code programs: 

* **1_box.nc** - fill one box of vials
* **2_boxes.nc** - fill two boxes of vials

1. Open **fill_boxes.py** for editing:
```
sudo nano /home/pi/robot/py/fill_boxes.py
```

2. Near the top of the file (line 32 onwards) are various settings to be modified:

```

# SETTINGS
# modify values of variables in this section to match your system

# filenames
filename1Box = '/home/pi/robot/nc/1_box.nc'
filename2Boxes = '/home/pi/robot/nc/2_boxes.nc'

# home/datum + homing pull-off (mm) (value of Grbl setting $27)
x_home = -5
y_home = -5
z_home = -5

# z value providing minimal clearance between nozzle and top of vials
z_fill = -62 

# peristaltic pump settings
fill_time = 0.43
# pause to allow for drips before moving to next vial
drip_pause = 0.1 

# vial coordinates (x,y)
box1FrontLeft = (-8,-14)
box1BackRight = (-236,-240)
box2FrontLeft = (-8,-286)
box2BackRight = (-236,-513)

nrows=10
ncols=10
nVials=nrows*ncols
```

* **filename1Box** and **filename2Boxes** specify the filename and full path to the two G-code programs that will be generated. You should not need to modify these values. The GUI script (**/home/pi/robot/py/fly_gui.py**) expects the two programs to have the default names and paths; if you alter the names or paths of these files, you will need to edit the GUI script.
* The parameters **x_home, y_home** and **z_home** are the Cartesian coordinates of the home position (*i.e.* home/datum + homing pull-off (mm)). 
* Modify **z_fill** to the appropriate nozzle height for filling vials (this was determined in step 5 of section \@ref(boxCoordinates)). 
* **fill_time** was determined in the previous section \@ref(calibratePump).
* The default value of **drip_pause** should be appropriate for most systems.
* The vial coordinates (**box1FrontLeft**, **box1BackRight**, **box2FrontLeft** and **box2BackRight**) were determined in section \@ref(boxCoordinates).
* Our boxes have ten rows, each containing ten vials, so we set **nrows** and **ncols** to 10.

3. After editing the settings in **fill_boxes.py**, run the script to generate the two G-code programs:
```
./robot/py/fill_boxes.py
```

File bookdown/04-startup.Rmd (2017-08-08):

# System start-up {#startup}

## Attach Norprene tubing

1. Attach the nozzle end of the Norprene tubing to the holder on the Z-axis actuator using releasable cable ties (figure \@ref(fig:attachNozzle)).

```{r attachNozzle, echo=FALSE, out.width='75%', fig.align='center', fig.cap="Attachment of nozzle end of tubing to the Z-axis actuator."}
knitr::include_graphics("images/pump4.jpg")
```

2. Attach the Masterflex Norprene tubing to the right-hand side vertical post using a releasable cable tie. Ensure there is a large loop in the tubing between this attachment point and the nozzle so that the x-axis actuator can move freely (figure \@ref(fig:tubingPost))

```{r tubingPost, echo=FALSE, out.width='75%', fig.align='center', fig.cap="Attachment of Norprene tubing to the right-hand side vertical post."}
knitr::include_graphics("images/pump5.jpg")
```

3. Feed the tubing through the peristaltic pump (figure \@ref(fig:tubingPump)) and into your vat of fly food (figure \@ref(fig:flyFoodVat)).

```{r tubingPump, echo=FALSE, out.width='75%', fig.align='center', fig.cap="Norprene tubing passing through peristaltic pump."}
knitr::include_graphics("images/pump6.jpg")
```

```{r flyFoodVat, echo=FALSE, out.width='75%', fig.align='center', fig.cap="Vat of fly food."}
knitr::include_graphics("images/pump7.jpg")
```

## Switch on all devices
 * power supply unit for gShield and motors
 * raspberry pi
 * peristaltic pump
 
## Prime pump 
 * Position a beaker under the nozzle  (figure \@ref(fig:primeBeaker)).
 * Press and hold the prime button on the front of the peristaltic pump until a continuous stream of fly food is pumped into the beaker (figure \@ref(fig:primeButton))

```{r primeBeaker, echo=FALSE, out.width='75%', fig.align='center', fig.cap="Positioning of beaker under nozzle to collect fly food expelled during priming of peristaltic pump."}
knitr::include_graphics("images/prime_beaker.jpg")
```

```{r primeButton, echo=FALSE, out.width='75%', fig.align='center', fig.cap="Prime button on peristaltic pump."}
knitr::include_graphics("images/prime_button.jpg")
```

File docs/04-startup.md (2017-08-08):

# System start-up {#startup}

## Attach Norprene tubing

1. Attach the nozzle end of the Norprene tubing to the holder on the Z-axis actuator using releasable cable ties (figure \@ref(fig:attachNozzle)).

<div class="figure" style="text-align: center">
Attachment of nozzle end of tubing to the Z-axis actuator.
<p class="caption">(\#fig:attachNozzle)Attachment of nozzle end of tubing to the Z-axis actuator.</p>
</div>

2. Attach the Masterflex Norprene tubing to the right-hand side vertical post using a releasable cable tie. Ensure there is a large loop in the tubing between this attachment point and the nozzle so that the x-axis actuator can move freely (figure \@ref(fig:tubingPost))

<div class="figure" style="text-align: center">
Attachment of Norprene tubing to the right-hand side vertical post.
<p class="caption">(\#fig:tubingPost)Attachment of Norprene tubing to the right-hand side vertical post.</p>
</div>

3. Feed the tubing through the peristaltic pump (figure \@ref(fig:tubingPump)) and into your vat of fly food (figure \@ref(fig:flyFoodVat)).

<div class="figure" style="text-align: center">
Norprene tubing passing through peristaltic pump.
<p class="caption">(\#fig:tubingPump)Norprene tubing passing through peristaltic pump.</p>
</div>

<div class="figure" style="text-align: center">
Vat of fly food.
<p class="caption">(\#fig:flyFoodVat)Vat of fly food.</p>
</div>

## Switch on all devices
 * power supply unit for gShield and motors
 * raspberry pi
 * peristaltic pump
 
## Prime pump 
 * Position a beaker under the nozzle  (figure \@ref(fig:primeBeaker)).
 * Press and hold the prime button on the front of the peristaltic pump until a continuous stream of fly food is pumped into the beaker (figure \@ref(fig:primeButton))

<div class="figure" style="text-align: center">
Positioning of beaker under nozzle to collect fly food expelled during priming of peristaltic pump.
<p class="caption">(\#fig:primeBeaker)Positioning of beaker under nozzle to collect fly food expelled during priming of peristaltic pump.</p>
</div>

<div class="figure" style="text-align: center">
Prime button on peristaltic pump.
<p class="caption">(\#fig:primeButton)Prime button on peristaltic pump.</p>
</div>

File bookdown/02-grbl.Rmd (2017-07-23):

# Grbl installation and configuration {#grbl}

## Overview

CNC motion control is provided by grbl (https://github.com/gnea/grbl), an open source, embedded, high performance g-code parser. Grbl is written in optimized C and runs directly on an Arduino. This is used in conjunction with the gShield (formerly known as grblshield) which provides the hardware drivers for the stepper motors. Grbl sends out TTL signals on pins A3 and 13 of the Arduino to control coolant flow and spindle direction, respectively. Here these signals are used to remotely control a peristaltic pump. 

## Flashing Grbl to Arduino

To flash Grbl to the Arduino you will need a computer with the latest version of the [Arduino IDE](https://www.arduino.cc/en/Main/Software) installed. The following instructions for flashing Grbl to the Arduino are taken from: https://github.com/gnea/grbl/wiki/Compiling-Grbl

_**NOTE: Before starting, delete prior Grbl library installations from the Arduino IDE. Otherwise, you'll have compiling issues! On a Mac, Arduino libraries are located in ```~/Documents/Arduino/libraries/```. On Windows, it's in ```My Documents\Arduino\libraries```.**_

1. Download the Grbl source code.
 * Open the following page in your web browser: https://github.com/gnea/grbl
 * Click on the ```<>Code``` Tab
 * Click the ```Clone or Download``` green button on the Grbl home page.
 * Click the ```Download ZIP```
 * Unzip the download and you'll have a folder called ```grbl-XXX```, where `XXX` is the release version. 

2. Launch the Arduino IDE (figure \@ref(fig:arduinoIDE))
 * Make sure you are using the most recent version of the Arduino IDE!

```{r arduinoIDE, echo=FALSE, out.width='75%', fig.align='center', fig.cap="Arduino IDE"}
knitr::include_graphics("images/arduino_IDE.png")
```

3. Load Grbl into the Arduino IDE as a Library.
 * Click the ```Sketch``` drop-down menu, navigate to ```Include Library``` and select ```Add .ZIP Library```.
 * **IMPORTANT:** Select the ```Grbl``` folder **_inside_** the ```grbl-XXX``` folder, which **only** contains the source files and an example directory (figure \@ref(fig:addGrblLib)).
 
```{r addGrblLib, echo=FALSE, out.width='75%', fig.align='center', fig.cap="Loading Grbl library into the Arduino IDE"}
knitr::include_graphics("images/add_grbl_lib.png")
```

 * If you accidentally select the `.zip` file or the wrong folder, you will need to navigate to your Arduino library, delete the mistake, and re-do Step 3.
 
4. Open the `GrblUpload` Arduino example.
 * Click the ```File``` drop-down menu, navigate to ```Examples->Grbl```, and select ```GrblUpload``` (figure \@ref(fig:grblUploadFile)).

```{r grblUploadFile, echo=FALSE, out.width='75%', fig.align='center', fig.cap="GrblUpload example file"}
knitr::include_graphics("images/grbl_upload_file.png")
```

5. Compile and upload Grbl to your Arduino.
 * Connect your computer directly to the Arduino using the USB cable. Unplug the USB cable from the raspberry pi and plug it into your computer. Remember to reconnect the raspberry pi to the Arduino after you have finished configuring Grbl (figure \@ref(fig:laptop2arduino)).

```{r laptop2arduino, echo=FALSE, out.width='75%', fig.align='center', fig.cap="Laptop connected directly to Arduino"}
knitr::include_graphics("images/laptop_connected_to_arduino.jpg")
```

 * Make sure your board is set to the Arduino Uno in the ```Tool->Board``` menu and the serial port is selected correctly in ```Tool->Serial Port```. 
 * Click the ```Upload```, and Grbl should compile and flash to your Arduino! (Flashing with a programmer also works by using the ```Upload Using Programmer``` menu command.)

## Check serial connection to Grbl

_**NOTE: Before powering up the gShield and motors, check that the actuator carriages for all three axes are approximately centred (figure \@ref(fig:actuatorsCentred)). Initially we do not know in which direction the actuator carriages will travel when G-code commands are issued, so positioning each in the middle of its range reduces the risk of collisions with the end stops.**_

```{r actuatorsCentred, echo=FALSE, out.width='75%', fig.align='center', fig.cap="Actuator carriages centred in preparation for powering-up motors for first time"}
knitr::include_graphics("images/actuator_carriages_centred.jpg")
```

1. Open serial monitor in Arduino IDE
 * Click ```Tools``` drop-down menu, and select ```Serial Monitor```

```{r serialMonitor, echo=FALSE, out.width='75%', fig.align='center', fig.cap="Arduino IDE Serial Monitor"}
knitr::include_graphics("images/Arduino_IDE_serial_monitor.png")
```

 * Note that line-ending is set to ```Carriage return``` and baud rate is set to ```115200``` (figure \@ref(fig:serialMonitor))
2. Try issuing a G-code command. 
 * Type ```?``` and hit return. 
 * This command will report the current position; as we have just started the system up all axes will be at 0.000.
3. Now try moving actuators
 * To move in the x-axis type ```x5``` and hit return. Make a note of the direction in which the actuator carriage moves. N.B. this command tells Grbl to move to the x coordinate that is 5 units from the origin, it is not equivalent to telling the robot to move 5 units in the x-axis.
 * To move in the opposite direction along the x-axis type ```x-5``` and hit return.
 * To return to the starting point, use ```x0```
 * Repeat for the other axes, replacing the x in the commands with y or z. Make a note of the direction the actuator carriages move with each command.

## Grbl configuration

### Read current configuration
 * The ```$$``` command will report Grbl's current configuration.
 * Descriptions of these settings can be found here: https://github.com/gnea/grbl/wiki/Grbl-v1.1-Configuration
 * These settings will be modified in subsequent steps.

### Check directionality of each axis.

```{r robotOrientation, echo=FALSE, out.width='75%', fig.align='center', fig.cap="Orientation of robot."}
knitr::include_graphics("images/robot_orientation.png")
```

 * Orientation of the robot is shown in figure \@ref(fig:robotOrientation).
 * At present the origins of all three axes are mid-way along each actuator, because this was the position of the actuator carriages when the system was started.
 * Make sure actuator carriages are at their current origin by entering this command: ```x0y0z0```
 * Enter the command: ```x5```. The x-axis carriage should move from right to left (orientation of robot is shown in figure \@ref(fig:robotOrientation). If it doesn't, make a note that it will need to be inverted.
 * Enter the command: ```y5```. The y-axis carriage should move forwards. If it doesn't, make a note that it will need to be inverted.
 * Enter the command: ```z5```. The z-axis carriage should move up. If it doesn't, make a note that it will need to be inverted.
 * The direction of the actuators can be inverted using setting **$3**, the [Direction port invert (mask)](https://github.com/gnea/grbl/wiki/Grbl-v1.1-Configuration#3--direction-port-invert-mask). An appropriate value is selected from table \@ref(tab:invertMaskSettings). For example, to invert the direction of the X and Z axis actuators use the following command: ```$3=5```

<!---
Table: (\#tab:invertMaskSettings) Masks for direction port inversion.

| Setting Value | Mask |Invert X | Invert Y | Invert Z |
|:-------------:|:----:|:-------:|:--------:|:--------:|
| 0 | 00000000 |N | N | N |
| 1 | 00000001 |Y | N | N |
| 2 | 00000010 |N | Y | N |
| 3 | 00000011 |Y | Y | N |
| 4 | 00000100 |N | N | Y |
| 5 | 00000101 |Y | N | Y |
| 6 | 00000110 |N | Y | Y |
| 7 | 00000111 |Y | Y | Y |

 --->
```{r invertMaskSettings, echo=FALSE}
setting <- 0:7
mask <- c("00000000", "00000001", "00000010", "00000011", "00000100", "00000101", "00000110", "00000111")
invX <- rep(c("N", "Y"),4)
invY <- rep(c("N", "N", "Y", "Y"),2)
invZ <- c(rep(c("N"),4), rep(c("Y"),4))
masks <- as.data.frame(cbind(setting, mask, invX, invY, invZ))
names(masks) <- c("Setting Value", "Mask", "Invert X", "Invert Y", "Invert Z")
knitr::kable(
  masks, booktabs = TRUE,
  caption = 'Masks for direction port inversion.'
)
```

### Activate hard limits
Hard limits are a safety feature to prevent the machine from travelling beyond the limits of travel. Grbl monitors the paired limit switches on each axis and if a switch is triggered it will immediately switch off all motors. Hard limits are activated by setting **$21** [hard limits ( boolean)](https://github.com/gnea/grbl/wiki/Grbl-v1.1-Configuration#21---hard-limits-boolean) to 1: 
```
$21=1
```

### Setup homing
The homing cycle is used to set the origin of the Cartesian coordinate system used by the robot. During the homing cycle Grbl moves each actuator in the positive direction until the limit switches are triggered. The homing cycle is activated by setting **$22** [homing cycle (boolean)](https://github.com/gnea/grbl/wiki/Grbl-v1.1-Configuration#22---homing-cycle-boolean) to 1: 
```
$22=1
```

Initiate  a homing cycle using the following command: ```$h```. All actuator carriages should move to the origin of their axes. The origin of the Cartesian coordinate system (home) for the robot is shown in figures \@ref(fig:xyOrigin) and \@ref(fig:zOrigin)

```{r xyOrigin, echo=FALSE, out.width='75%', fig.align='center', fig.cap="Origin of XY coordinate system."}
knitr::include_graphics("images/xy_origin.jpg")
```

```{r zOrigin, echo=FALSE, out.width='75%', fig.align='center', fig.cap="Origin of Z axis."}
knitr::include_graphics("images/z_origin.jpg")
```

We also need to set **$24** [homing feed rate](https://github.com/gnea/grbl/wiki/Grbl-v1.1-Configuration#24---homing-feed-mmmin) and **$25** [homing seek rate](https://github.com/gnea/grbl/wiki/Grbl-v1.1-Configuration#25---homing-seek-mmmin). Homing seek rate is the initial speed at which Grbl searches for the limit switches. Once it has them, it makes slower approach at the homing feed rate to get a more precise location for machine zero. We will set homing seek rate to 1000 mm/min ```$24=100``` and homing feed rate to 100 mm/min ```$25=1000```.

At the end of a homing cycle each actuator carriage must be moved off its home limit switch, otherwise the hard limit will be triggered. 
The **$27** [Homing pull-off (mm)](https://github.com/gnea/grbl/wiki/Grbl-v1.1-Configuration#27---homing-pull-off-mm) specifies the distance required to clear the limit switches. For our robot we will use a value of 5mm:
```
$27=5
```

### Motor step size
**$100**, **$101** and **$102** define [[X,Y,Z] steps/mm](https://github.com/gnea/grbl/wiki/Grbl-v1.1-Configuration#100-101-and-102--xyz-stepsmm).
Suitable values for our stepper motors are:
```
$100=40
$101=40
$102=49.673
```

If you are using a different type of stepper motor, the step size can be easily calculated by measuring how far each actuator moves in response to a G-code command. For example, we would calculate the step size for the X actuator as follows.

1. Using the serial monitor in the Arduino IDE, issue the following command to *home* the machine:
```
$h
```

2. Read the current position of the machine, as reported by the Grbl controller:
```
?
```
After homing the Cartesian coordinates should be zero minus the homing pull-off:
* x = -5
* y = -5
* z = -5

3. Make a note of the physical position of the nozzle.

4. Issue a g-code command to move to the -100mm position on the x-axis:
```
x-100
```
Keep decreasing the value of x until the x-actuator carriage almost meets the limit switch on the right hand side of the machine. The greater the distance moved, the more precise our calculation of step-size will be.

5. Query Grbl's machine coordinates:
```
?
```

6. Measure the physical distance travelled along the x-axis in millimetres.

7. Find **$100**, the currently configured step size for the x-axis:
```
$$
```

8. Calculate the correct value for step-size:

```
current_step_size = steps/mm in current configuration
grbl_start = start position reported by Grbl controller (mm)
grbl_end = end position reported by Grbl controller (mm)
physical_distance = physical distance moved by actuator (mm)

steps/mm = -(curr_steps_per_mm * (end_pos_grbl-start_pos_grbl)) / physical_distance
```

### Feed rates and acceleration
**$110**, **$111** and **$112** set the [maximum rates (mm/min)](https://github.com/gnea/grbl/wiki/Grbl-v1.1-Configuration#110-111-and-112--xyz-max-rate-mmmin) for the X, Y and Z actuators, respectively. We will use the following values:
```
$110=5000
$111=5000
$112=2500
```

[Acceleration (mm/sec^2)](https://github.com/gnea/grbl/wiki/Grbl-v1.1-Configuration#120-121-122--xyz-acceleration-mmsec2) is set to 50 for all axes:
```
$120=50
$121=50
$122=50
```
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

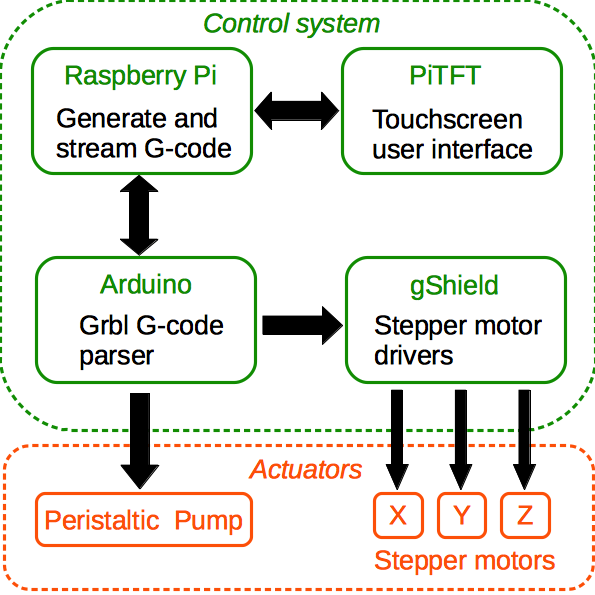
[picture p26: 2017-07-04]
bookdown/images/system_architecture.png

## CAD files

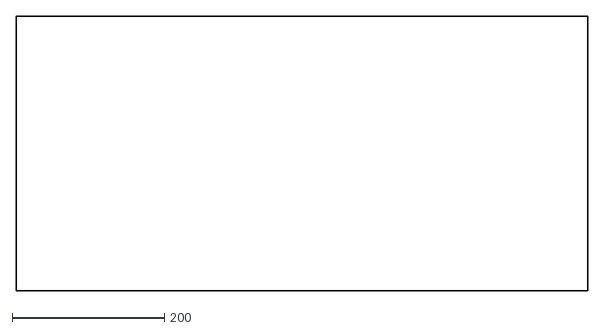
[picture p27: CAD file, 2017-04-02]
docubricks/base_board_v2.dxf
749.9 x 359.9

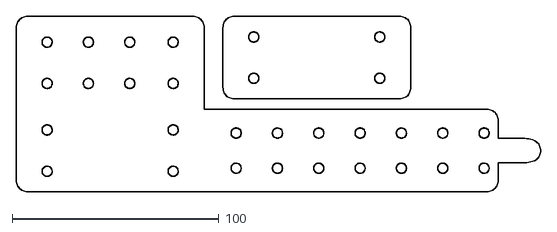
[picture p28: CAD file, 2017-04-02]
docubricks/tube_mount_v2.dxf
253.9 x 85.0

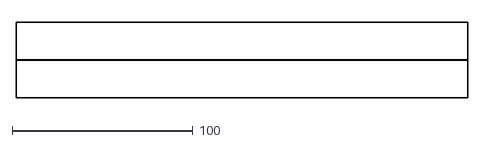
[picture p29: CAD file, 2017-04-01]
docubricks/fence.dxf
250.0 x 42.0

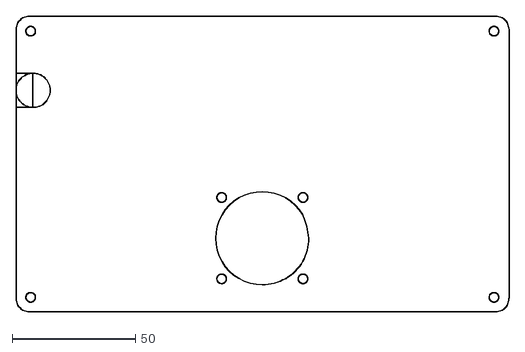
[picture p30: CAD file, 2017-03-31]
docubricks/box_lid.dxf
200.0 x 120.0

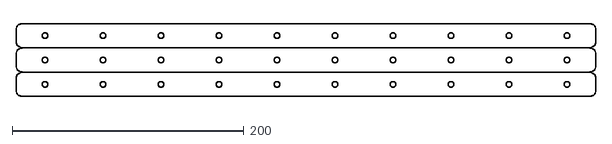
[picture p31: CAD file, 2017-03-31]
docubricks/500mm_guide_rails.dxf
499.9 x 62.9

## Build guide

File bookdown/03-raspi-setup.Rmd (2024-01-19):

# Raspberry Pi setup {#raspi}

## Overview
The raspberry pi is used to generate, then stream g-code to the Arduino. A small thin-film-transistor (TFT) touchscreen serves as the user interface to the raspberry pi. 

## Install image
~~The first step is to install Adafruit's custom raspberry pi image on the micro SD card. The custom image is described here:~~

~~```https://learn.adafruit.com/adafruit-pitft-28-inch-resistive-touchscreen-display-raspberry-pi/easy-install```~~

~~We want the classic version which boots into X by default, rather then the lite version that boots to the command line. The classic version can be downloaded from this link:~~

~~```https://s3.amazonaws.com/adafruit-raspberry-pi/2016-10-18-pitft-28r.zip```~~

Adafruit's custom raspberry pi image is no longer available. I have created an image (pitft.img) based on Adafruit's original that is preconfigured for use with the robot. It can be downloaded from:

https://zenodo.org/records/10534021

Instructions on installing images on SD cards can be found here:

https://www.raspberrypi.org/documentation/installation/installing-images/

## Network configuration
The small screen of the pitft makes using most applications quite tricky. Therefore the first thing we should do after installing the image is configure networking, so that we can access the raspberry pi remotely using ssh.

To set a static IP address for the ethernet adapter, edit the following lines of ```/etc/dhcpcd.conf```:

```
interface eth0

static ip_address=192.168.1.3/24
static routers=192.168.1.254
static domain_name_servers=192.168.1.254
```

**ip_address**, **routers** and **domain_name_servers** should be set to values appropriate for your network.

To raspberry pi can then be accessed using ssh, *e.g.*:
```
  ssh pi@192.168.1.3
```

The default password for the **pi** user account is **raspberry**

## Install minicom

*N.B. Minicom is pre-installed on my pitft.img*

Minicom is useful for manual control of the robot and for editing grbl settings. 

To install minicom run these two commands:

```
sudo apt-get update
sudo apt-get install minicom
```

Before we can use minicom we need to enable serial:

```
sudo nano /boot/config.txt
```

Change the last line of this file from

```
enable_uart=0
```

to

```
enable_uart=1
```

If you have not already done so, reconnect the raspberry pi to the arduino using the USB cable. To use minicom to connect to the grbl controller running on the arduino, use:

```
sudo minicom -D /dev/ttyACM0 -b115200
```

## Expand filesystem
Expand filesystem on micro SD card:

```
    sudo raspi-config
    (expand filesystem)
    sudo reboot
```

## Install python scripts {#installScripts}
*N.B. The python scripts are pre-installed on my pitft.img*

Make sure you are in pi's home directory:

```
cd
```

Download and unpack robot.tar.gz

```
curl -O https://raw.githubusercontent.com/WaylandM/fly-food-robot/master/raspberrypi/robot.tar.gz
tar xzvf robot.tar.gz
```

The **robot** directory contains two subdirectories: **nc** (g-code scripts) and **py** (python scripts).

To automatically launch the robot GUI when the raspberry pi starts up, we need to edit the autostart file for the pi user:

```
sudo nano /home/pi/.config/lxsession/LXDE-pi/autostart
```

Add the following line to autostart:

```
@/home/pi/robot/py/fly_gui.py
```

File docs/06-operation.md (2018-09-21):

# Routine operation {#operation}

## Prepare system

Instructions for starting the system are provided in chapter \@ref(startup).

## Fill boxes
Load boxes onto platform as described in section \@ref(loadBoxes).

From the touchscreen menu select **1 Box** or **2 Boxes** depending on the number of boxes on the platform (figure \@ref(fig:touchscreen)). The robot will **home** to zero the cartesian coordinate system, and then commence filling the vials. 

<div class="figure" style="text-align: center">
Touchscreen interface.
<p class="caption">(\#fig:touchscreen)Touchscreen interface.</p>
</div>

During filling the robot can be stopped by clicking on the **Stop** button (figure \@ref(fig:stopRobot)).

<div class="figure" style="text-align: center">
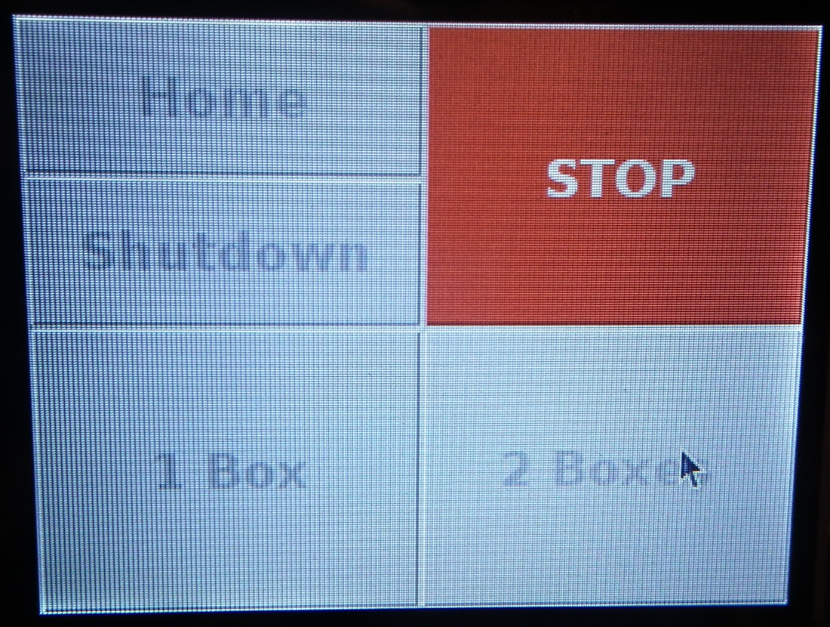
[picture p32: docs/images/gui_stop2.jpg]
Appearance of touchscreen interface when a job is running.

<p class="caption">(\#fig:stopRobot)Appearance of touchscreen interface when a job is running.</p>
</div>

## Shutdown

* The raspberry pi should be shutdown using the **shutdown** button on the touchscreen. 
* The Norprene tubing should be removed from the vat of fly food, then any food remaining in the tubing can be expelled by pressing and holding the **prime** button on the peristaltic pump. Ensure there is a receptacle under the nozzle to catch the expelled fly food. The Norprene tubing should be removed from the robot for cleaning/sterilization. 
* All devices (raspberry pi, power supply unit for gShield and motors, and peristaltic pump) should be switched off.
* The robot can be wiped clean if necessary using a damp cloth. The platform can be removed for thorough cleaning.

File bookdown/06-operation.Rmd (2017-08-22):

# Routine operation {#operation}

## Prepare system

Instructions for starting the system are provided in chapter \@ref(startup).

## Fill boxes
Load boxes onto platform as described in section \@ref(loadBoxes).

From the touchscreen menu select **1 Box** or **2 Boxes** depending on the number of boxes on the platform (figure \@ref(fig:touchscreen)). The robot will **home** to zero the cartesian coordinate system, and then commence filling the vials. 

```{r touchscreen, echo=FALSE, out.width='60%', fig.align='center', fig.cap="Touchscreen interface."}
knitr::include_graphics("images/gui.jpg")
```

During filling the robot can be stopped by clicking on the **Stop** button (figure \@ref(fig:stopRobot)).

```{r stopRobot, echo=FALSE, out.width='60%', fig.align='center', fig.cap="Appearance of touchscreen interface when a job is running."}
knitr::include_graphics("images/gui_stop2.jpg")
```

## Shutdown

* The raspberry pi should be shutdown using the **shutdown** button on the touchscreen. 
* The Norprene tubing should be removed from the vat of fly food, then any food remaining in the tubing can be expelled by pressing and holding the **prime** button on the peristaltic pump. Ensure there is a receptacle under the nozzle to catch the expelled fly food. The Norprene tubing should be removed from the robot for cleaning/sterilization. 
* All devices (raspberry pi, power supply unit for gShield and motors, and peristaltic pump) should be switched off.
* The robot can be wiped clean if necessary using a damp cloth. The platform can be removed for thorough cleaning.

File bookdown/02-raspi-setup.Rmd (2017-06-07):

# Raspberry Pi setup

https://learn.adafruit.com/adafruit-pitft-28-inch-resistive-touchscreen-display-raspberry-pi/easy-install

https://s3.amazonaws.com/adafruit-raspberry-pi/2016-10-18-pitft-28r.zip

https://www.raspberrypi.org/documentation/installation/installing-images/

```
    sudo raspi-config
    (expand filesystem)
    sudo reboot
```

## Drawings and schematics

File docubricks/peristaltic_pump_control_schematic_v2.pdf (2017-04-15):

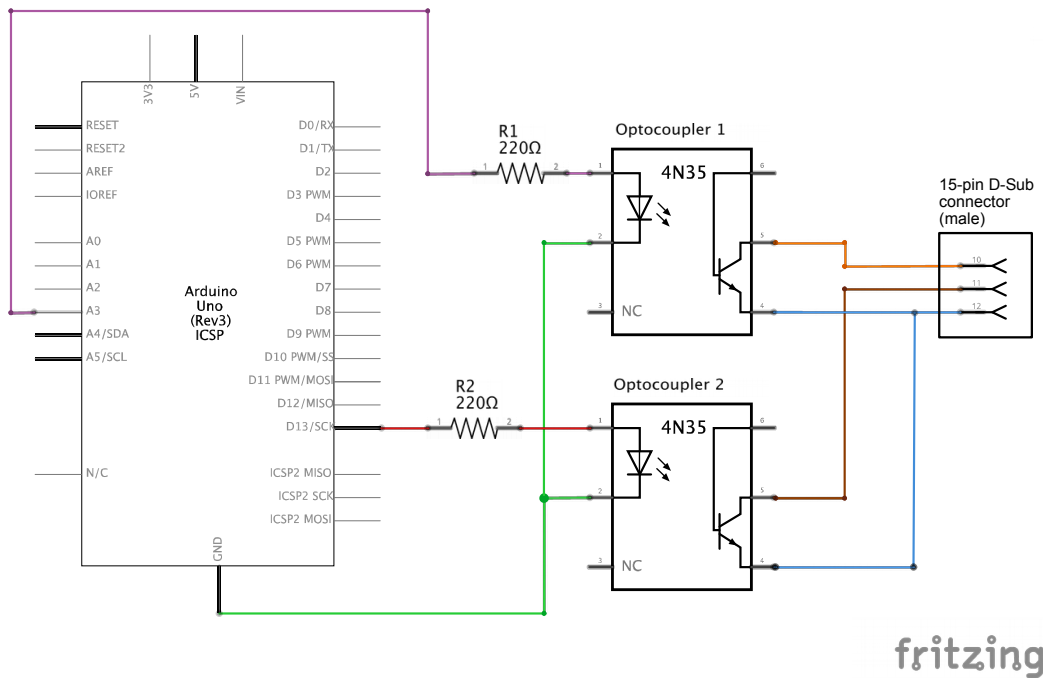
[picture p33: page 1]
15-pin D-Sub connector (male)

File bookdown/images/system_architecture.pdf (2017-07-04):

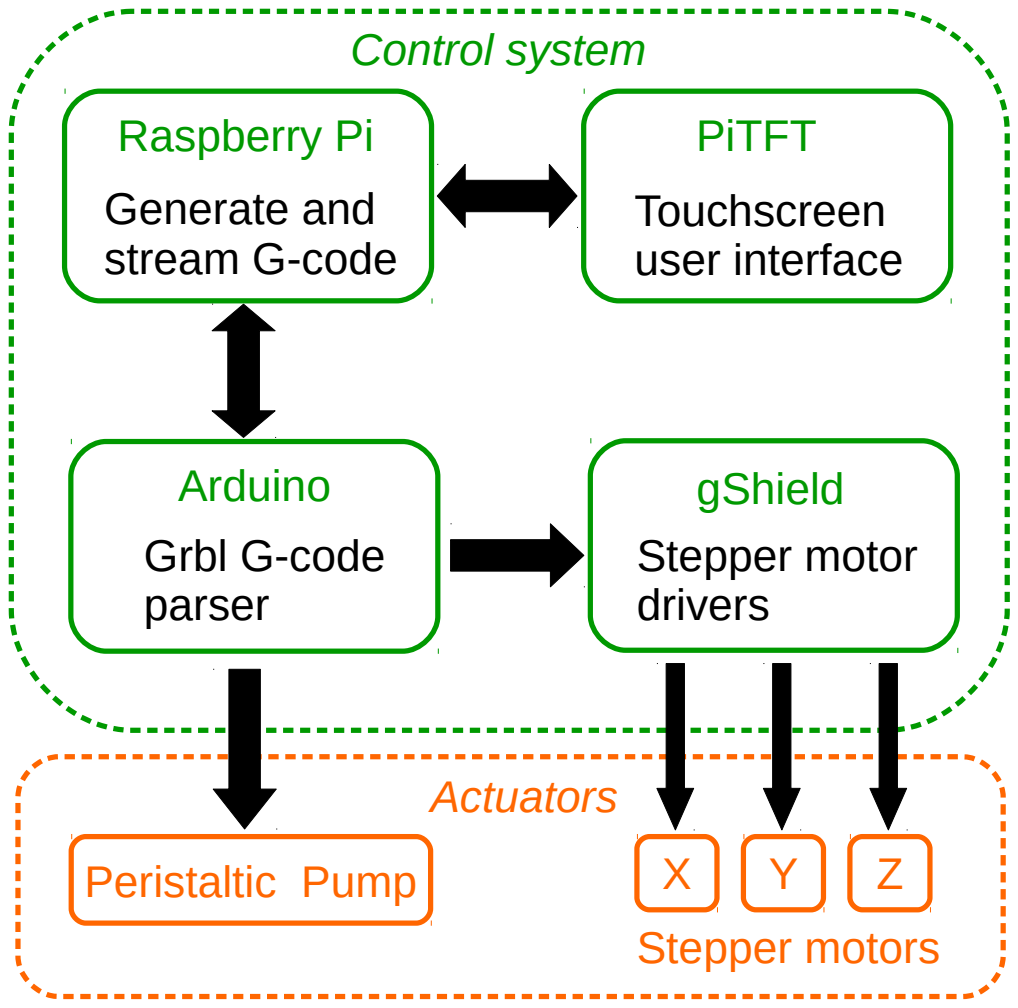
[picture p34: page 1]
Raspberry Pi; PiTFT; Arduino; gShield; Peristaltic Pump; Stepper motors; Generate and stream G-code; Touchscreen user interface; Stepper motor drivers; Grbl G-code parser; Control system; Actuators

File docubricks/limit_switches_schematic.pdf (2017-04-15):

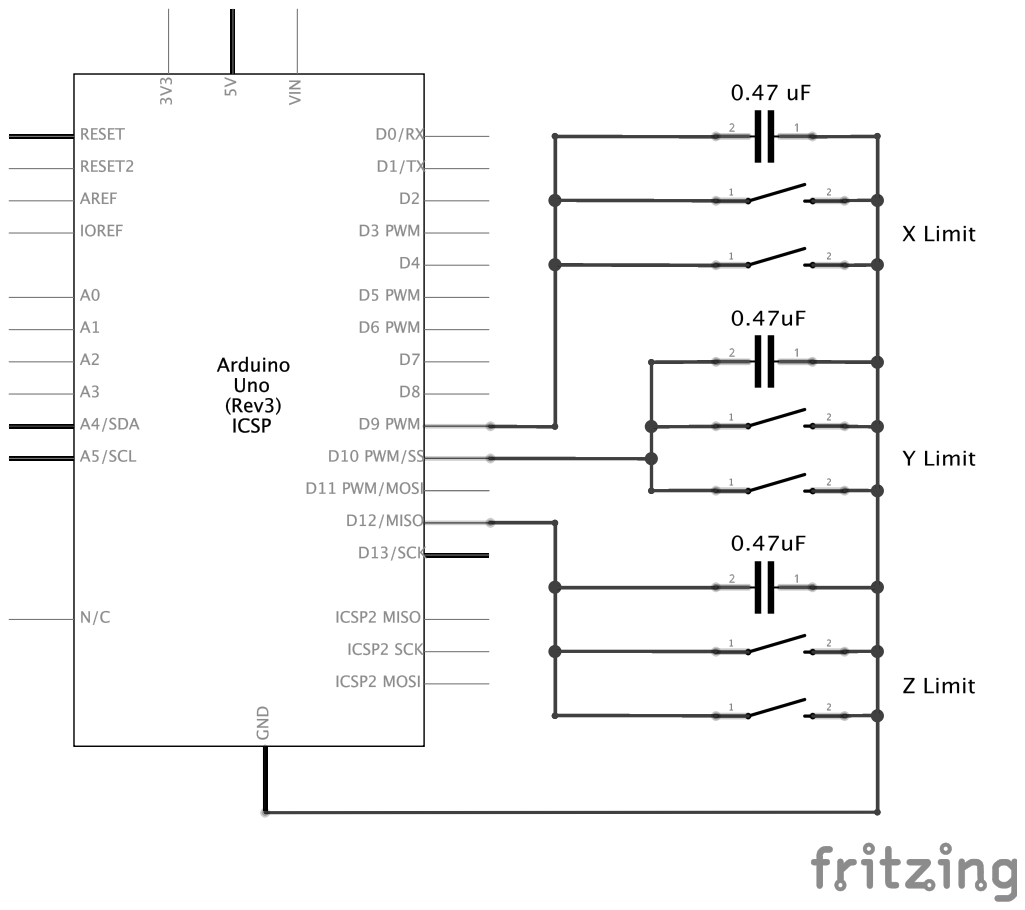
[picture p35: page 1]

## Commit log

2017-03-24 new file: docubricks/V-Slot-Gantry-Plate.jpg new file: docubricks/Y-T-nut-in-foot.jpg new file: docubricks/Y-actuator-adj-pulley.jpg new file: docubricks/Y-actuator-and-rail-components.jpg new file: 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
2017-03-25 new file: docubricks/attach_xz1.jpg new file: docubricks/attach_xz2.jpg new file: docubricks/attach_xz3.jpg new file: docubricks/attach_xz4.jpg new file: docubricks/attach_xz5.jpg new file: docubrick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
2017-03-28 new file: docubricks/Y-actuator-complete.jpg modified: docubricks/attach_xz1.jpg modified: docubricks/attach_xz2.jpg new file: docubricks/ctrl_box_strut1.jpg new file: docubricks/ctrl_box_strut2.jpg 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
2017-03-31 new file: docubricks/500mm_guide_rails.dxf new file: docubricks/500mm_guide_rails.png new file: docubricks/500mm_guide_rails.svg new file: docubricks/box_lid.dxf new file: docubricks/box_lid.png new 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
    [500mm_guide_rails.dxf, box_lid.dxf, fence.dxf]
2017-04-01 modified: docubricks/fence.dxf modified: docubricks/fence.png modified: docubricks/fence.svg
    [fence.dxf]
2017-04-02 new file: docubricks/base_board_v2.dxf new file: docubricks/base_board_v2.png new file: docubricks/base_board_v2.svg new file: docubricks/box_lid.svg new file: docubricks/tube_mount_v2.dxf new file: 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
    [base_board_v2.dxf, tube_mount_v2.dxf]
2017-04-06 new file: docubricks/electronics.jpg modified: docubricks/project.docubricks.xml new file: docubricks/tube_mount1.jpg new file: docubricks/tube_mount2.jpg new file: docubricks/tube_mount3.jpg new fil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
2017-04-06 modified: docubricks/project.docubricks.xml new file: docubricks/pump1.jpg new file: docubricks/pump2.jpg new file: docubricks/pump3.jpg new file: docubricks/pump4.jpg new file: docubricks/pump5.jpg 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
2017-04-06 modified: docubricks/project.docubricks.xml new file: docubricks/psu1.jpg new file: docubricks/psu2.jpg new file: docubricks/raspberryPi.jpg
2017-04-06 new file: docubricks/arduino_mounting_components.jpg new file: docubricks/arduino_mounting_holes.jpg new file: docubricks/box_and_lid.jpg new file: docubricks/box_lhs.jpg new file: docubricks/box_mou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
2017-04-18 new file: docubricks/M2_bolt_in_V-slot.jpg modified: docubricks/project.docubricks.xml new file: docubricks/wire_in_V-slot_1.jpg new file: docubricks/wire_in_V-slot_2.jpg
2017-04-19 new file: docubricks/motor-cable1.jpg new file: docubricks/motor-cable2.jpg new file: docubricks/motor-cable3.jpg new file: docubricks/motor-cable4.jpg new file: docubricks/motor-cable5.jpg new file: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
2017-06-05 new file: .gitignore new file: bookdown/.Rbuildignore new file: bookdown/01-intro.Rmd new file: bookdown/02-software-installation.Rmd new file: bookdown/03-calibration.Rmd new file: bookdown/04-opera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
2017-06-07 new file: bookdown/02-raspi-setup.Rmd deleted: bookdown/02-software-installation.Rmd deleted: bookdown/03-calibration.Rmd new file: bookdown/03-grbl.Rmd new file: bookdown/04-g-code.Rmd deleted: book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
2017-06-18 modified: bookdown/01-intro.Rmd new file: bookdown/02-grbl.Rmd deleted: bookdown/03-grbl.Rmd renamed: bookdown/02-raspi-setup.Rmd -> bookdown/03-raspi-setup.Rmd new file: bookdown/images/actuator_car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
2017-06-18 modified: bookdown/02-grbl.Rmd new file: bookdown/images/arduino_IDE_serial_monitor.png new file: bookdown/images/arduino_IDE_serial_monitor.tiff modified: docs/02-grbl.md modified: docs/creating-job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
2017-07-02 modified: bookdown/02-grbl.Rmd modified: bookdown/03-raspi-setup.Rmd modified: docs/03-raspi-setup.md modified: docs/creating-jobs-in-g-code.html modified: docs/grbl-installation-and-configuration.ht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
2017-07-02 new file: raspberrypi/robot.zip
2017-07-02 modified: bookdown/03-raspi-setup.Rmd deleted: raspberrypi/robot.zip
2017-07-02 modified: raspberrypi/robot.tar.gz modified: raspberrypi/robot/py/fly_gui.py
2017-07-03 modified: bookdown/01-intro.Rmd modified: bookdown/02-grbl.Rmd modified: bookdown/03-raspi-setup.Rmd modified: docs/01-intro.md modified: docs/02-grbl.md modified: docs/03-raspi-setup.md modified: do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
2017-07-03 modified: bookdown/02-grbl.Rmd modified: bookdown/03-raspi-setup.Rmd modified: docs/02-grbl.md modified: docs/03-raspi-setup.md modified: docs/06-references.md modified: docs/creating-jobs-in-g-code.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
2017-07-03 modified: raspberrypi/robot.tar.gz modified: raspberrypi/robot/py/calibrate_pump.py modified: raspberrypi/robot/py/fill_boxes.py modified: raspberrypi/robot/py/stream2.py
2017-07-03 modified: raspberrypi/robot.tar.gz
2017-07-03 modified: raspberrypi/robot.tar.gz modified: raspberrypi/robot/py/calibrate_pump.py modified: raspberrypi/robot/py/fill_boxes.py
2017-07-03 modified: raspberrypi/robot.tar.gz modified: raspberrypi/robot/py/fill_boxes.py
2017-07-03 modified: bookdown/04-g-code.Rmd modified: raspberrypi/robot/py/fill_boxes.py
2017-07-03 modified: bookdown/04-g-code.Rmd modified: raspberrypi/robot.tar.gz
2017-07-24 modified: raspberrypi/robot/py/calibrate_pump.py modified: raspberrypi/robot/py/fill_boxes.py
2017-07-24 modified: bookdown/04-g-code.Rmd new file: bookdown/images/pump4.jpg new file: bookdown/images/pump5.jpg new file: bookdown/images/pump6.jpg new file: bookdown/images/pump7.jpg modified: docs/04-g-co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
2017-07-24 modified: bookdown/03-raspi-setup.Rmd modified: bookdown/04-g-code.Rmd modified: docs/01-intro.md modified: docs/02-grbl.md modified: docs/03-raspi-setup.md modified: docs/04-g-code.md modified: docs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
